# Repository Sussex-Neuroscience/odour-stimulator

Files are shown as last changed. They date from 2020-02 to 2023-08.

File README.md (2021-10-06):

# Odour stimulator - A fast, time precise open source system to deliver odours. 

## This open source stimulator is based on previous work by a different group. Their work is published  [here](https://www.pnas.org/content/111/47/16925), [here](https://www.sciencedirect.com/science/article/pii/S2589004218300646) and [here](<https://academic.oup.com/chemse/article/42/2/141/2709444>)

The image below is taken from https://academic.oup.com/chemse/article/42/2/141/2709444
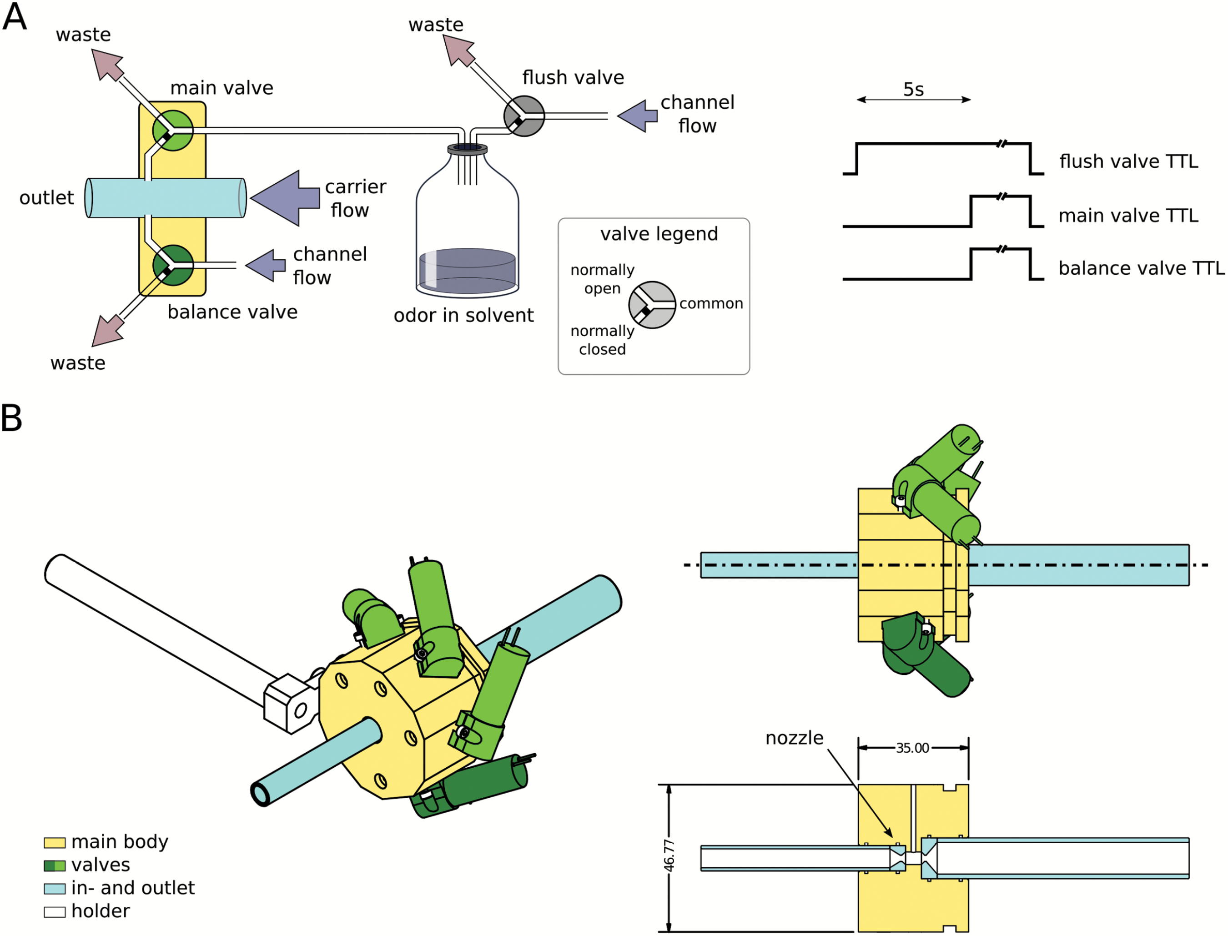
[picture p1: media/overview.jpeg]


--- 
## Some information about this project:

- developed as part of the work of the [Nowotny lab](https://www.sussex.ac.uk/research/centres/sussex-neuroscience/phd/4yearphd/supervisors/circuits-projects/thomas-nowotny-project) and it is being setup initially for experiments with flies. 
- The reason we are publicly documenting things is that since the original papers describing the stimulator came out, some enabling technology has become widely available, which makes setting this up simpler and less expensive. This write up is our attempt to document this.
- Some documentation of the orignal stimulator is already publicly available on [github already](https://github.com/grg2rsr/OlfactoryStimulator), unfortunately some of the schematics are only in PDF format (which prevents fast conversion to PCBs) and some of the CAD files are in a proprietary format, that officially can only be read with "Autodesk Inventor". Luckily there is a [plugin for FreeCad](https://github.com/jmplonka/InventorLoader/) that allows the conversion to a more open format.  This derivative will share orignal files that can be modified using open source sofware.

---

### main differences from the original papers:

- Since it would be quite expensive to reproduce the PEEK machined part they describe on the paper, we bought polypropylene filament and we printing the part. There are a couple of differences in between the two processes, and the derivatitve designs we made are optimised for printing. 
  
- Several online resources show tips and guides on how to print with this material:
 - https://www.lpfrg.com/guides/3d-printing-polypropylene/
 - https://all3dp.com/2/3d-printing-polypropylene-how-to-3d-print-with-pp/
 - https://www.simplify3d.com/support/materials-guide/polypropylene/
 - https://www.youtube.com/watch?v=yRw2mC_6A00 

- The electronics in this project but emphasis on using a microncontroller for timing control and connectivity with other devices. More specifically we are using an ESP32 and micropython to integrate the system with other devices/computers.

### repository structure:

#### repository link: https://github.com/Sussex-Neuroscience/odour-stimulator

#### tags: 
hardware,behaviour,electrophysiology,drosophila

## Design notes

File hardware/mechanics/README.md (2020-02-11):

# mechanical parts (tube fixtures, air stream nozzles, etc)

---
#### the folder [from_raiser_et_al](/from_raiser_et_al) contains the files from the github repo of the mentioned paper. They are proprietary files that can only be read with "Autodesk inventor". 

#### The content of the folder are as follows:

|File Name| Description|
|---|---|
|Assembly1.iam|Autodesk Inventor assembly that includes the spatial configuration of all the .ipt files|
|body.ipt|Main body file|
|holder.ipt|Holder for the main body|
|nozzle_big.ipt|Big nozzle placed in the main body|
|nozzle_small.ipt|Small nozzle placed in the main body|
|rod.ipt|Generic mounting rod, connects to the holder|
|table1.xls|Table summarizing the performance of the stimulator|
|tube.ipt|Glass tube, used in the Assembly1.iam for graphical purposes|
|tube_lont.ipt|Glass tube, used in the Assembly1.iam for graphical purposes|
|valve.ipt|The valve, redrawn for graphical purposes in the Assembly1.iam|

---
#### the folder [freeCad_conversion](/from_raiser_et_al/freeCad_conversion) contains the translation of those files, so that they can be opened with FreeCad. 

- this conversion is done using the following library: <https://github.com/jmplonka/InventorLoader/>

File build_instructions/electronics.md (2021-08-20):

[M4x10 screws]:parts.yaml#M4x10PanSteel
[3D printer]:parts.yaml#3DPrinter
[printed block]:parts.yaml#PrintedBlock

# Electronics

## electronic boards 

This system relies on the [BeeHive project]() for its electronic components. 

For this stimulator we are using mainly two different electronic circuits, one central hub, and some "Spike and hold" solenoid controllers.

- The central hub is responsible for receiving power, command controls from a PC and sending appropriate timing signals to the "Spike and hold" solenoid controllers.  

- The Spike and hold solenoid controllers are receiving 3.3V (or 5V) pulses that turn on the solenoid valves. The circuitry is based on a design by the solenoid manufacturer, which can be found [here](https://www.theleeco.com/engineering/electrical-engineering/lee-solenoid-valve-drive-circuit-schematics/).  
    - Briefly, the circuit generates a short fast voltage signal (spike phase) that is higher than the rating of the solenoid valve (in this case 24V), this allows for better repeatability in opening times of the solenoid as well as faster opening. When the spike phase is over, the voltage signal going to the solenoid drops down to the nominal rate of the valves (in this case 12V), which is enough to keep the valves open and avoid overheat. Once the signal to keep the valve open is done, the circuit generates a negative voltage signal that also closes the solenoid faster and more reliably.
    - An schematic fo the signal going to the solenoids can be found below (taken from the LEE company website):
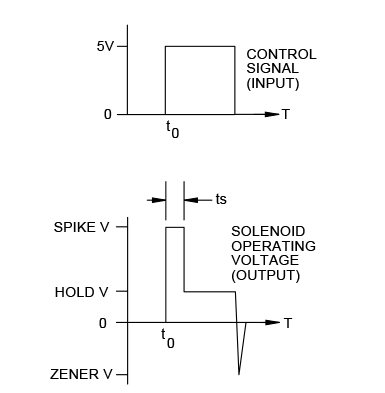
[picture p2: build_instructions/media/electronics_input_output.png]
      

{{BOM}}

## Method
This page should have some instructions for things in your project instead it just has a link for three [M4x10 screws]{Qty: 3} and another link to use [two more][M4x10 screws]{Qty: 2}.

[one block][printed block]{Qty: 1}

[3D printer][3D printer]{Qty: 1, Cat: tool}

[two more][M4x10 screws]{Qty: 2}

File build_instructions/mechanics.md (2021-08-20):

[M4x10 screws]:parts.yaml#M4x10PanSteel
[rotameterS]:parts.yaml#RotameterS
[rotameterM]:parts.yaml#RotameterM

# Mechanics

For the mechanical part of the project we are using mainly:  

- Rotameters     
- PFTE Tubing   
- Y or T connectors for the PFTE tubing     
- 3D Printed block  
- Glass tube    
- Metal plate to secure rotameters  
- holder for the printed block  

## Method
This page should have some instructions for things in your project instead it just has a link for three [M4x10 screws]{Qty: 3} and another link to use [two more][M4x10 screws]{Qty: 2}.

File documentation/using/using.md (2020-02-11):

#### use this document to guide people on using this device.

Some guidelines on what to put in this document:

1. Getting started

 - what the device should look like, things to prepare and watch out for before turning it on.

2. Turning everything on, making sure it is functioning as it should.

3. calibration steps

4. maintenance/storage information.

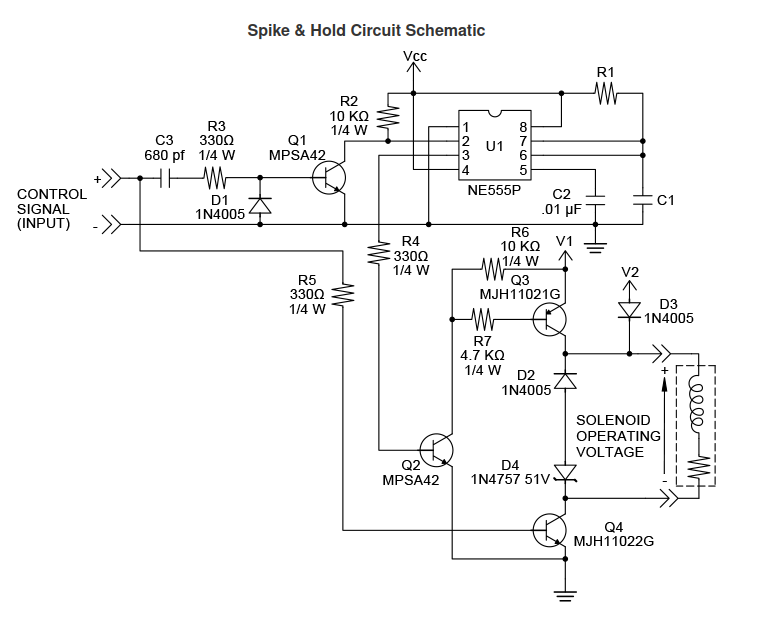
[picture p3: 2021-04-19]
media/schematics_overview.png

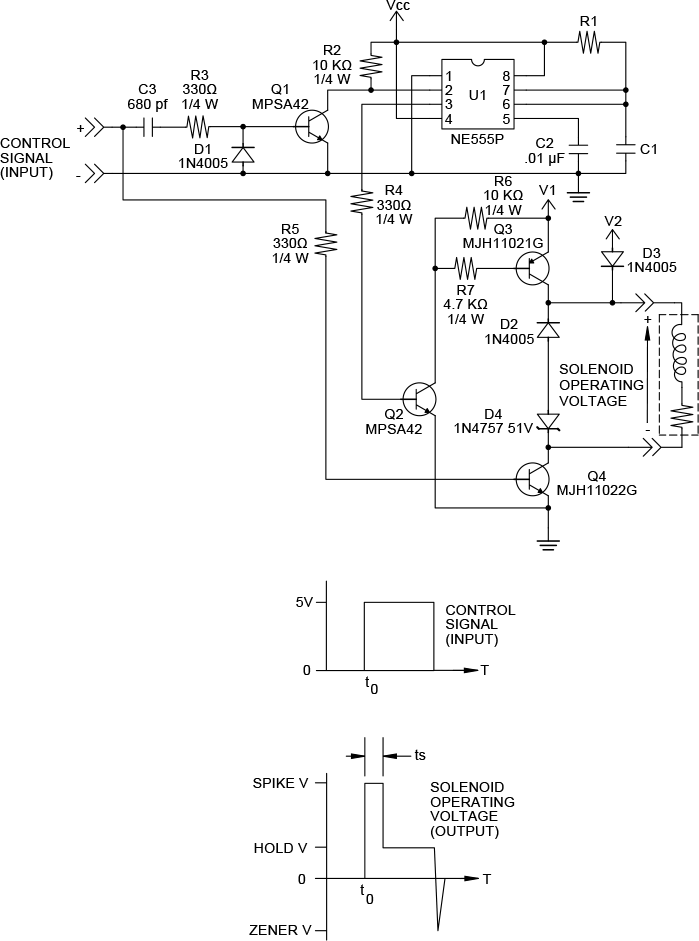
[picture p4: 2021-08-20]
media/engineering_spike-hold-circuit-schematic.png

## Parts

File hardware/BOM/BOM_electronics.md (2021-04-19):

#

| Reference | Qty  | Description | manufacturer  |MPN|Link|
|---|---|---|---|---|---|
|Solenoid valves | 5  | fast actuation 3 way solenoid valve |    [Lee](https://www.theleeco.com/)   |LHDA1221411H |<https://www.theleeco.com/products/electro-fluidic-systems/solenoid-valves/control-valves/lhd-series/3-port/face-mount/>|
|Ribbon cable| 5 metres| 10 lines ribbon cable (better if coloured) |RS components|214-0661 |<https://uk.rs-online.com/web/p/flat-ribbon-cable/2140661/>|
|electronic pressure control| 1 | ~0-3 bar, capacity > 10 L/min (the more the better, can be used for several setups)|Analyt-mtc|35898|<https://analyt-mtc.de/en/>|
|Rotameter| 1 | 0-5000ml/min|Analyt-mtc|102-05-N saphir|<https://analyt-mtc.de/en/>|
|Rotameter| 7 (at least) | 0-350ml/min|Analyt-mtc|112-02 glas|<https://analyt-mtc.de/en/>|

<br>

---
### PCB

|References              |Qty|Description                                                                        |Manufacturer     |MPN              |Manufacturer    |MPN     |Manufacturer|MPN|Manufacturer|MPN|Digikey           |Mouser|RS |Newark|Farnell|
|------------------------|---|-----------------------------------------------------------------------------------|-----------------|-----------------|----------------|--------|------------|---|------------|---|------------------|------|---|------|-------|
|C1, C2                  |2  |C Small 680pF Unpolarized capacitor, small symbol Disc D5.1mm W3.2mm P5.00mm       |Vishay           |K681K10X7RF5UH5  |                |        |            |   |            |   |BC2690CT-ND       |      |   |      |       |
|C3, C4                  |2  |C Small 10nF Unpolarized capacitor, small symbol Disc D5.1mm W3.2mm P5.00mm        |TDK corporation  |FA18C0G2A103JRU06|                |        |            |   |            |   |445-175393-1-ND   |      |   |      |       |
|C5, C6                  |2  |C Small 10µF Unpolarized capacitor, small symbol Disc D5.1mm W3.2mm P5.00mm        |AVX              |TAP106M035SCS    |                |        |            |   |            |   |478-6062-ND       |      |   |      |       |
|C11                     |1  |CP Small 680µF Polarized capacitor, small symbol Radial D10.0mm P5.00mm            |Rubycon          |35PX680MEFC10X16 |                |        |            |   |            |   |1189-1282-ND      |      |   |      |       |
|C15                     |1  |CP Small 220µF Polarized capacitor, small symbol Radial D10.0mm P5.00mm            |Panasonic        |EEU-FM1V221      |                |        |            |   |            |   |P12411-ND         |      |   |      |       |
|D1, D5, D3, D2, D6, D4  |6  |1N4005 50V 1A General Purpose Rectifier Diode, DO-41 D SOD81 P10.16mm Horizontal   |micro commercial |1N4005-TP        |                |        |            |   |            |   |1N4005-TPMSCT-ND  |      |   |      |       |
|D7, D8                  |2  |1N47xxA 1300mW Zener Diode, DO-41 D SOD81 P10.16mm Horizontal                      |Vishay           |1N4757A-TR       |                |        |            |   |            |   |1N4757AVSCT-ND    |      |   |      |       |
|D17                     |1  |1N5820 20V 3A Schottky Barrier Rectifier Diode, DO-201AD D P15.24mm Horizontal     |SMC              |SB5100TA         |                |        |            |   |            |   |1655-1524-1-ND    |      |   |      |       |
|H4, H3, H1, H2          |4  |MountingHole Mounting Hole without connection 3.2mm M3                             |                 |                 |                |        |            |   |            |   |                  |      |   |      |       |
|J1, J2                  |2  |Conn 01x02 Female single row, 01x02 P2.54mm Vertical                               |Sullins          |PPTC101LFBN-RC   |                |        |            |   |            |   |S7008-ND          |      |   |      |       |
|J3, J4                  |2  |Screw Terminal 01x02 P2.54mm Vertical                                              |                 |                 |                |        |            |   |            |   |                  |      |   |      |       |
|J9                      |1  |Barrel Jack MountingPin DC with a mounting pin 5.5mmODx2.1mmID PJ-202A             |CUI devices      |PJ-202AH         |                |        |            |   |            |   |CP-202AH-ND       |      |   |      |       |
|L1                      |1  |L 33µH Inductor Radial D7.5mm P3.50mm Fastron 07P                                  |Wuerth           |7447471330       |                |        |            |   |            |   |732-3415-ND       |      |   |      |       |
|Q1, Q2                  |2  |Q PNP Darlington BCE MJH11021G transistor, base/collector/emitter TO-247-3 Vertical|ON semiconductors|MJH11021G        |                |        |            |   |            |   |MJH11021GOS-ND    |      |   |      |       |
|Q5, Q6, Q3, Q4          |4  |MPSA42 TRANS NPN 300V 0.5A TO-92 TO-92L Inline Wide                                |ON semiconductors|MPSA42           |ON semiconductor|KSP42BU |            |   |            |   |KSP42BU-ND        |      |   |      |       |
|Q7, Q8                  |2  |Q NPN Darlington BCE MJH11022G transistor, base/collector/emitter TO-247-3 Vertical|ON semiconductors|MJH11022G        |                |        |            |   |            |   |MJH11022GOS-ND    |      |   |      |       |
|R1, R9, R2, R10         |4  |R Small 10k Resistor, small symbol Axial DIN0411 L9.9mm D3.6mm P12.70mm Horizontal |Stackpole        |CF14JT10K0       |                |        |            |   |            |   |CF14JT10K0CT-ND   |      |   |      |       |
|R3, R4                  |2  |R Small 4.7k Resistor, small symbol Axial DIN0411 L9.9mm D3.6mm P12.70mm Horizontal|Stackpole        |CF14JT4K70       |                |        |            |   |            |   |CF14JT4K70CT-ND   |      |   |      |       |
|R7, R11, R5, R8, R12, R6|6  |R Small 330 Resistor, small symbol Axial DIN0411 L9.9mm D3.6mm P12.70mm Horizontal |Stackpole        |CF14JT330R       |                |        |            |   |            |   |CF14JT330RCT-ND   |      |   |      |       |
|R13, R14                |2  |R Small 2k Resistor, small symbol Axial DIN0411 L9.9mm D3.6mm P12.70mm Horizontal  |Stackpole        |CF14JT2K00       |                |        |            |   |            |   |CF14JT2K00CT-ND   |      |   |      |       |
|R15                     |1  |R Small 1k Resistor, small symbol Axial DIN0411 L9.9mm D3.6mm P12.70mm Horizontal  |Stackpole        |CF14JT1K00       |                |        |            |   |            |   |CF14JT1K00CT-ND   |      |   |      |       |
|R16                     |1  |R Small 9.1k Resistor, small symbol Axial DIN0411 L9.9mm D3.6mm P12.70mm Horizontal|Stackpole        |RNMF14FAD9K10    |                |        |            |   |            |   |RNMF14FAD9K10CT-ND|      |   |      |       |
|U1, U2                  |2  |LM555xM Precision Timers, 555 compatible, SOIC-8 DIP-8 W7.62mm LongPads            |Texas instruments|NA555P           |                |        |            |   |            |   |296-21753-5-ND    |      |   |      |       |
|U5                      |1  |LM2596T-ADJ 12V 3A 150kHz Step-Down Voltage Regulator, TO-220 TO-220-5             |Texas instruments|LM2596T-ADJ/LF02 |                |        |            |   |            |   |296-49677-ND      |      |   |      |       |

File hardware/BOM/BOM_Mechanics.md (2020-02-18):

#

## Glossary

ID - Internal diametre  
OD - External diametre

| Reference | Qty  | Description | supplier  |MPN|Link|
|---|---|---|---|---|---|
|Female Luer | 14  | x10-32 UNF thread, PC - (polycarbonate?) seems to be this <https://www.fishersci.co.uk/shop/products/polycarbonate-luer-fitting-1/11746008> | novodirect   |YO-45501-60|company website leads to <https://www.fishersci.co.uk/gb/en/home.html>|
|Male Luer Adapter| 40 pieces | luer to tube adapter (~1.2mm ID or ~1/16 inch) |Cole-Parmer|15252400 |<https://www.fishersci.co.uk/shop/products/polypropylene-male-luer-adapters-4/15252400>|
|Teflon tubing|X metres|original from paper has been discontinued. 4mm ID 5mm OD is what comes closer |[VWR](<https://uk.vwr.com>)|DENE3400405|<https://uk.vwr.com/store/product/576865/tubing-ptfe>|
|Teflon tubing|10 metres|original from paper has been discontinued. 1mm ID 2mm OD is what comes closer |[VWR](<https://uk.vwr.com>)|DENE3400102|<https://uk.vwr.com/store/product/576865/tubing-ptfe>|
|Y shaped connector|20|for 4mm ID tubing|[VWR](<https://uk.vwr.com>)|229-0723|https://uk.vwr.com/store/catalog/product.jsp?catalog_number=229-0723|
|Tube clamps| 20 |stepless flow control|[VWR](<https://uk.vwr.com>) |229-0117|<https://uk.vwr.com/store/product/7652160/tubing-clamps-stop-it>|
|Glass vials | 20 |12 ml glass vials (preferentially with rubber/silicone lid) |[VWR](<https://uk.vwr.com>) | 548-0820|<https://uk.vwr.com/store/catalog/product.jsp?catalog_number=548-0820>|
|Glass vials caps| 20 |screw caps with rubber/silicone part for needle entry |[VWR](<https://uk.vwr.com>) | 548-3335|<https://uk.vwr.com/store/catalog/product.jsp?catalog_number=548-0820>|
| Needles | 100 |18G X 1 1/2 |[VWR](<https://uk.vwr.com>) |613-5396|<https://uk.vwr.com/store/product/16614798/hypodermic-needles-aganitm>|
| Needles | 20|14G 2X40mm |[VWR](<https://uk.vwr.com>) | HSWA8300013707 |<https://uk.vwr.com/store/product/7210520/hypodermic-needles-fine-ject-for-single-use>|
| O-ring | 1 | 12mm ID 15mm OD silicone  |[RS](<https://uk.rs-online.com>) | 0128849 |<https://uk.rs-online.com/web/p/seals-o-rings/0128849/>|
| O-ring | 1 | 7.5mm ID 11mm OD silicone |[RS](<https://uk.rs-online.com>) | 5279790 |<https://uk.rs-online.com/web/p/seals-o-rings/5279790/>|

glass tube 7 mm ID, 10 mm OD, 80 mm length  
glass tube 4 mm ID, 7 mm OD, 80 mm length  

#### note : The rows indicated with !! are as on the original bill of materials, but they seem to be a duplicate entry.

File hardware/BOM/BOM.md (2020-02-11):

#### Create BOM files for the equipment

e recommend creating different files:

<br>
- Electronic_BOM.csv: table containing all the integrated circuits(IC) necessary to populate the PCB (when one is present). We suggest using the format used by [kitspace.org](kitspace.org), so that people can easily order parts from different manufacturers.
<br>

<br>

- Mechanical_BOM.csv: Table containing all the mechanical parts necessary to build the equipment. Include here screws, printed parts, tubes, etc. See example below for fields

<br>

|part name| function  | quantity  |  obs.  |supplier|supplier number|link|
|---|---|---|---|---|---|---|
|M6x1 hex screws | used for holding motor in place  | 5  |  these could be substituted by flathead screws  |digikey| RPC6208-ND |<https://www.digikey.co.uk/product-detail/en/essentra-components/SHSM6L16A/RPC6208-ND/9343049> |

<br>

- Tools_BOM.csv: table containing all tools used for the build. Pliers, hammer, etc.

<br>

|part name| function  | quantity  |  obs.  |supplier|supplier number|link|
|---|---|---|---|---|---|---|
|Nose needle Pliers  | hold components while soldering  | 1  |    regular pliers would also work   |digikey|L4VN-ND  |<https://www.digikey.co.uk/product-detail/en/apex-tool-group/L4VN/L4VN-ND/8021129> |

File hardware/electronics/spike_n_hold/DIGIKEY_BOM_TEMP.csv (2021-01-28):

Reference | Value | Footprint | Datasheet | Category | DK_Datasheet_Link | DK_Detail_Page | Description | Digi-Key_PN | Family | MPN | Manufacturer | Status
Q1 | MJH11021G |  | ~
Q7 | MJH11022G |  | ~
R3 | 4.7k |  | ~
R1 | 10k |  | ~
R7 | 330 |  | ~
D1 | 1N4005 | Diode_THT:D_DO-41_SOD81_P10.16mm_Horizontal | http://www.vishay.com/docs/88503/1n4001.pdf
D5 | 1N4005 | Diode_THT:D_DO-41_SOD81_P10.16mm_Horizontal | http://www.vishay.com/docs/88503/1n4001.pdf
D7 | 1N47xxA | Diode_THT:D_DO-41_SOD81_P10.16mm_Horizontal | https://www.vishay.com/docs/85816/1n4728a.pdf
J3 | to_solenoid_2 | Connector_PinHeader_2.54mm:PinHeader_1x02_P2.54mm_Vertical | ~
R11 | 330 |  | ~
Q5 | MPSA42 | digikey-footprints:TO-92-3 | https://www.onsemi.com/pub/Collateral/MPSA42-D.PDF | Discrete Semiconductor Products | https://www.onsemi.com/pub/Collateral/MPSA42-D.PDF | /product-detail/en/on-semiconductor/MPSA42/MPSA42FS-ND/32397 | TRANS NPN 300V 0.5A TO-92 | MPSA42FS-ND | Transistors - Bipolar (BJT) - Single | MPSA42 | ON Semiconductor | Active
Q3 | MPSA42 | Package_TO_SOT_THT:TO-92_Inline | http://www.onsemi.com/pub_link/Collateral/MPSA42-D.PDF
D3 | 1N4005 | Diode_THT:D_DO-41_SOD81_P10.16mm_Horizontal | http://www.vishay.com/docs/88503/1n4001.pdf
R5 | 330 |  | ~
J1 | input_trigger_2 | Connector_PinHeader_2.54mm:PinHeader_1x02_P2.54mm_Vertical | ~
C1 | 680pF | Capacitor_THT:C_Disc_D5.1mm_W3.2mm_P5.00mm | ~
C5 | 10µF |  | ~
C3 | 10nF |  | ~
U1 | LM555xM | Package_DIP:DIP-8_W7.62mm_LongPads | http://www.ti.com/lit/ds/symlink/lm555.pdf
R9 | 10k |  | ~
R13 | 2k |  | ~
Q9 | MJH11021G |  | ~
Q15 | MJH11022G |  | ~
R16 | 4.7k |  | ~
R15 | 10k |  | ~
R21 | 330 |  | ~
D9 | 1N4005 | Diode_THT:D_DO-41_SOD81_P10.16mm_Horizontal | http://www.vishay.com/docs/88503/1n4001.pdf
D12 | 1N4005 | Diode_THT:D_DO-41_SOD81_P10.16mm_Horizontal | http://www.vishay.com/docs/88503/1n4001.pdf
D15 | 1N47xxA | Diode_THT:D_DO-41_SOD81_P10.16mm_Horizontal | https://www.vishay.com/docs/85816/1n4728a.pdf
J7 | to_solenoid_4 | Connector_PinHeader_2.54mm:PinHeader_1x02_P2.54mm_Vertical | ~
R25 | 330 |  | ~
Q13 | MPSA42 | digikey-footprints:TO-92-3 | https://www.onsemi.com/pub/Collateral/MPSA42-D.PDF | Discrete Semiconductor Products | https://www.onsemi.com/pub/Collateral/MPSA42-D.PDF | /product-detail/en/on-semiconductor/MPSA42/MPSA42FS-ND/32397 | TRANS NPN 300V 0.5A TO-92 | MPSA42FS-ND | Transistors - Bipolar (BJT) - Single | MPSA42 | ON Semiconductor | Active
Q11 | MPSA42 | Package_TO_SOT_THT:TO-92_Inline | http://www.onsemi.com/pub_link/Collateral/MPSA42-D.PDF
D10 | 1N4005 | Diode_THT:D_DO-41_SOD81_P10.16mm_Horizontal | http://www.vishay.com/docs/88503/1n4001.pdf
R19 | 330 |  | ~
J5 | input_trigger_4 | Connector_PinHeader_2.54mm:PinHeader_1x02_P2.54mm_Vertical | ~
C7 | 680pF | Capacitor_THT:C_Disc_D5.1mm_W3.2mm_P5.00mm | ~
C12 | 10µF |  | ~
C9 | 10nF |  | ~
U3 | LM555xM | Package_DIP:DIP-8_W7.62mm_LongPads | http://www.ti.com/lit/ds/symlink/lm555.pdf
R22 | 10k |  | ~
R27 | 2k |  | ~
Q17 | MJH11021G |  | ~
Q23 | MJH11022G |  | ~
R31 | 4.7k |  | ~
R29 | 10k |  | ~
R35 | 330 |  | ~
D18 | 1N4005 | Diode_THT:D_DO-41_SOD81_P10.16mm_Horizontal | http://www.vishay.com/docs/88503/1n4001.pdf
D22 | 1N4005 | Diode_THT:D_DO-41_SOD81_P10.16mm_Horizontal | http://www.vishay.com/docs/88503/1n4001.pdf
D24 | 1N47xxA | Diode_THT:D_DO-41_SOD81_P10.16mm_Horizontal | https://www.vishay.com/docs/85816/1n4728a.pdf
J12 | to_solenoid_6 | Connector_PinHeader_2.54mm:PinHeader_1x02_P2.54mm_Vertical | ~
R39 | 330 |  | ~
Q21 | MPSA42 | digikey-footprints:TO-92-3 | https://www.onsemi.com/pub/Collateral/MPSA42-D.PDF | Discrete Semiconductor Products | https://www.onsemi.com/pub/Collateral/MPSA42-D.PDF | /product-detail/en/on-semiconductor/MPSA42/MPSA42FS-ND/32397 | TRANS NPN 300V 0.5A TO-92 | MPSA42FS-ND | Transistors - Bipolar (BJT) - Single | MPSA42 | ON Semiconductor | Active
Q19 | MPSA42 | Package_TO_SOT_THT:TO-92_Inline | http://www.onsemi.com/pub_link/Collateral/MPSA42-D.PDF
D19 | 1N4005 | Diode_THT:D_DO-41_SOD81_P10.16mm_Horizontal | http://www.vishay.com/docs/88503/1n4001.pdf
R33 | 330 |  | ~
J10 | input_trigger_6 | Connector_PinHeader_2.54mm:PinHeader_1x02_P2.54mm_Vertical | ~
C14 | 680pF | Capacitor_THT:C_Disc_D5.1mm_W3.2mm_P5.00mm | ~
C19 | 10µF |  | ~
C17 | 10nF |  | ~
U6 | LM555xM | Package_DIP:DIP-8_W7.62mm_LongPads | http://www.ti.com/lit/ds/symlink/lm555.pdf
R37 | 10k |  | ~
R41 | 2k |  | ~
Q2 | MJH11021G |  | ~
Q8 | MJH11022G |  | ~
R4 | 4.7k |  | ~
R2 | 10k |  | ~
R8 | 330 |  | ~
D2 | 1N4005 | Diode_THT:D_DO-41_SOD81_P10.16mm_Horizontal | http://www.vishay.com/docs/88503/1n4001.pdf
D6 | 1N4005 | Diode_THT:D_DO-41_SOD81_P10.16mm_Horizontal | http://www.vishay.com/docs/88503/1n4001.pdf
D8 | 1N47xxA | Diode_THT:D_DO-41_SOD81_P10.16mm_Horizontal | https://www.vishay.com/docs/85816/1n4728a.pdf
J4 | to_solenoid_1 | Connector_PinHeader_2.54mm:PinHeader_1x02_P2.54mm_Vertical | ~
R12 | 330 |  | ~
Q6 | MPSA42 | digikey-footprints:TO-92-3 | https://www.onsemi.com/pub/Collateral/MPSA42-D.PDF | Discrete Semiconductor Products | https://www.onsemi.com/pub/Collateral/MPSA42-D.PDF | /product-detail/en/on-semiconductor/MPSA42/MPSA42FS-ND/32397 | TRANS NPN 300V 0.5A TO-92 | MPSA42FS-ND | Transistors - Bipolar (BJT) - Single | MPSA42 | ON Semiconductor | Active
Q4 | MPSA42 | Package_TO_SOT_THT:TO-92_Inline | http://www.onsemi.com/pub_link/Collateral/MPSA42-D.PDF
D4 | 1N4005 | Diode_THT:D_DO-41_SOD81_P10.16mm_Horizontal | http://www.vishay.com/docs/88503/1n4001.pdf
R6 | 330 |  | ~
J2 | input_trigger_1 | Connector_PinHeader_2.54mm:PinHeader_1x02_P2.54mm_Vertical | ~
C2 | 680pF | Capacitor_THT:C_Disc_D5.1mm_W3.2mm_P5.00mm | ~
C6 | 10µF |  | ~
C4 | 10nF |  | ~
U2 | LM555xM | Package_DIP:DIP-8_W7.62mm_LongPads | http://www.ti.com/lit/ds/symlink/lm555.pdf
R10 | 10k |  | ~
R14 | 2k |  | ~
Q18 | MJH11021G |  | ~
Q24 | MJH11022G |  | ~
R32 | 4.7k |  | ~
R30 | 10k |  | ~
R36 | 330 |  | ~
D20 | 1N4005 | Diode_THT:D_DO-41_SOD81_P10.16mm_Horizontal | http://www.vishay.com/docs/88503/1n4001.pdf
D23 | 1N4005 | Diode_THT:D_DO-41_SOD81_P10.16mm_Horizontal | http://www.vishay.com/docs/88503/1n4001.pdf
D25 | 1N47xxA | Diode_THT:D_DO-41_SOD81_P10.16mm_Horizontal | https://www.vishay.com/docs/85816/1n4728a.pdf
J13 | to_solenoid_5 | Connector_PinHeader_2.54mm:PinHeader_1x02_P2.54mm_Vertical | ~
R40 | 330 |  | ~
Q22 | MPSA42 | digikey-footprints:TO-92-3 | https://www.onsemi.com/pub/Collateral/MPSA42-D.PDF | Discrete Semiconductor Products | https://www.onsemi.com/pub/Collateral/MPSA42-D.PDF | /product-detail/en/on-semiconductor/MPSA42/MPSA42FS-ND/32397 | TRANS NPN 300V 0.5A TO-92 | MPSA42FS-ND | Transistors - Bipolar (BJT) - Single | MPSA42 | ON Semiconductor | Active
Q20 | MPSA42 | Package_TO_SOT_THT:TO-92_Inline | http://www.onsemi.com/pub_link/Collateral/MPSA42-D.PDF
D21 | 1N4005 | Diode_THT:D_DO-41_SOD81_P10.16mm_Horizontal | http://www.vishay.com/docs/88503/1n4001.pdf
R34 | 330 |  | ~
J11 | input_trigger_5 | Connector_PinHeader_2.54mm:PinHeader_1x02_P2.54mm_Vertical | ~
C16 | 680pF | Capacitor_THT:C_Disc_D5.1mm_W3.2mm_P5.00mm | ~
C20 | 10µF |  | ~
C18 | 10nF |  | ~
U7 | LM555xM | Package_DIP:DIP-8_W7.62mm_LongPads | http://www.ti.com/lit/ds/symlink/lm555.pdf
R38 | 10k |  | ~
R42 | 2k |  | ~
Q10 | MJH11021G |  | ~
Q16 | MJH11022G |  | ~
R18 | 4.7k |  | ~
R17 | 10k |  | ~
R23 | 330 |  | ~
D11 | 1N4005 | Diode_THT:D_DO-41_SOD81_P10.16mm_Horizontal | http://www.vishay.com/docs/88503/1n4001.pdf
D14 | 1N4005 | Diode_THT:D_DO-41_SOD81_P10.16mm_Horizontal | http://www.vishay.com/docs/88503/1n4001.pdf
D16 | 1N47xxA | Diode_THT:D_DO-41_SOD81_P10.16mm_Horizontal | https://www.vishay.com/docs/85816/1n4728a.pdf
J8 | to_solenoid_3 | Connector_PinHeader_2.54mm:PinHeader_1x02_P2.54mm_Vertical | ~
R26 | 330 |  | ~
Q14 | MPSA42 | digikey-footprints:TO-92-3 | https://www.onsemi.com/pub/Collateral/MPSA42-D.PDF | Discrete Semiconductor Products | https://www.onsemi.com/pub/Collateral/MPSA42-D.PDF | /product-detail/en/on-semiconductor/MPSA42/MPSA42FS-ND/32397 | TRANS NPN 300V 0.5A TO-92 | MPSA42FS-ND | Transistors - Bipolar (BJT) - Single | MPSA42 | ON Semiconductor | Active
Q12 | MPSA42 | Package_TO_SOT_THT:TO-92_Inline | http://www.onsemi.com/pub_link/Collateral/MPSA42-D.PDF
D13 | 1N4005 | Diode_THT:D_DO-41_SOD81_P10.16mm_Horizontal | http://www.vishay.com/docs/88503/1n4001.pdf
R20 | 330 |  | ~
J6 | input_trigger_3 | Connector_PinHeader_2.54mm:PinHeader_1x02_P2.54mm_Vertical | ~
C8 | 680pF | Capacitor_THT:C_Disc_D5.1mm_W3.2mm_P5.00mm | ~
C13 | 10µF |  | ~
C10 | 10nF |  | ~
U4 | LM555xM | Package_DIP:DIP-8_W7.62mm_LongPads | http://www.ti.com/lit/ds/symlink/lm555.pdf
R24 | 10k |  | ~
R28 | 2k |  | ~
U5 | LM2596T-12 | Package_TO_SOT_THT:TO-220-5_P3.4x3.7mm_StaggerOdd_Lead3.8mm_Vertical | http://www.ti.com/lit/ds/symlink/lm2596.pdf
D17 | 1N5820 | Diode_THT:D_DO-201AD_P15.24mm_Horizontal | http://www.vishay.com/docs/88526/1n5820.pdf
L1 | 33µH | Inductor_THT:L_Radial_D7.5mm_P3.50mm_Fastron_07P | ~
C11 | 680µF |  | ~
C15 | 220µF |  | ~
J9 | Barrel_Jack_MountingPin | digikey:Barrel_Jack_5.5mmODx2.1mmID_PJ-202A | ~

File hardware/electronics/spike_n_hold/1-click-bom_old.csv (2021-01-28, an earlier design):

References | Qty | Description
C1, C7, C14, C2, C16, C8 | 6 | C Small 680pF Unpolarized capacitor, small symbol Disc D5.1mm W3.2mm P5.00mm | https://www.digikey.co.uk/product-detail/en/vishay-beyschlag-draloric-bc-components/K681K10X7RF5UH5/BC2690CT-ND/2356904
C3, C9, C17, C4, C18, C10 | 6 | C Small 10nF Unpolarized capacitor, small symbol | https://www.digikey.co.uk/product-detail/en/vishay-beyschlag-draloric-bc-components/K103K10X7RF5UH5/BC2662CT-ND/2356876
C5, C12, C19, C6, C20, C13 | 6 | C Small 10µF Unpolarized capacitor, small symbol
C11 | 1 | CP Small 680µF Polarized capacitor, small symbol
C15 | 1 | CP Small 220µF Polarized capacitor, small symbol
D1, D5, D3, D9, D12, D10, D18, D22, D19, D2, D6, D4, D20, D23, D21, D11, D14, D13 | 18 | 1N4005 50V 1A General Purpose Rectifier Diode, DO-41 D SOD81 P10.16mm Horizontal
D7, D15, D24, D8, D25, D16 | 6 | 1N47xxA 1300mW Zener Diode, DO-41 D SOD81 P10.16mm Horizontal
D17 | 1 | 1N5820 20V 3A Schottky Barrier Rectifier Diode, DO-201AD D P15.24mm Horizontal
J1 | 1 | Conn 01x02 Female input trigger 2 Generic connector, single row, 01x02, script generated (kicad-library-utils/schlib/autogen/connector/) PinHeader 1x02 P2.54mm Vertical
J2 | 1 | Conn 01x02 Female input trigger 1 Generic connector, single row, 01x02, script generated (kicad-library-utils/schlib/autogen/connector/) PinHeader 1x02 P2.54mm Vertical
J3 | 1 | Screw Terminal 01x02 to solenoid 2 Generic screw terminal, single row, 01x02, script generated (kicad-library-utils/schlib/autogen/connector/) PinHeader 1x02 P2.54mm Vertical
J4 | 1 | Screw Terminal 01x02 to solenoid 1 Generic screw terminal, single row, 01x02, script generated (kicad-library-utils/schlib/autogen/connector/) PinHeader 1x02 P2.54mm Vertical
J5 | 1 | Conn 01x02 Female input trigger 4 Generic connector, single row, 01x02, script generated (kicad-library-utils/schlib/autogen/connector/) PinHeader 1x02 P2.54mm Vertical
J6 | 1 | Conn 01x02 Female input trigger 3 Generic connector, single row, 01x02, script generated (kicad-library-utils/schlib/autogen/connector/) PinHeader 1x02 P2.54mm Vertical
J7 | 1 | Screw Terminal 01x02 to solenoid 4 Generic screw terminal, single row, 01x02, script generated (kicad-library-utils/schlib/autogen/connector/) PinHeader 1x02 P2.54mm Vertical
J8 | 1 | Screw Terminal 01x02 to solenoid 3 Generic screw terminal, single row, 01x02, script generated (kicad-library-utils/schlib/autogen/connector/) PinHeader 1x02 P2.54mm Vertical
J9 | 1 | Barrel Jack MountingPin DC with a mounting pin 5.5mmODx2.1mmID PJ-202A
J10 | 1 | Conn 01x02 Female input trigger 6 Generic connector, single row, 01x02, script generated (kicad-library-utils/schlib/autogen/connector/) PinHeader 1x02 P2.54mm Vertical
J11 | 1 | Conn 01x02 Female input trigger 5 Generic connector, single row, 01x02, script generated (kicad-library-utils/schlib/autogen/connector/) PinHeader 1x02 P2.54mm Vertical
J12 | 1 | Screw Terminal 01x02 to solenoid 6 Generic screw terminal, single row, 01x02, script generated (kicad-library-utils/schlib/autogen/connector/) PinHeader 1x02 P2.54mm Vertical
J13 | 1 | Screw Terminal 01x02 to solenoid 5 Generic screw terminal, single row, 01x02, script generated (kicad-library-utils/schlib/autogen/connector/) PinHeader 1x02 P2.54mm Vertical
L1 | 1 | L 33µH Inductor Radial D7.5mm P3.50mm Fastron 07P
Q1, Q9, Q17, Q2, Q18, Q10 | 6 | Q PNP Darlington BCE MJH11021G transistor, base/collector/emitter | https://www.digikey.co.uk/products/en?keywords=MJH11021G
Q3, Q11, Q19, Q4, Q20, Q12 | 6 | MPSA42 0.5A Ic, 300V Vce, NPN High Voltage Transistor, TO-92 Inline
Q5, Q13, Q21, Q6, Q22, Q14 | 6 | MPSA42 TRANS NPN 300V 0.5A TO-92 TO-92-3
Q7, Q15, Q23, Q8, Q24, Q16 | 6 | Q NPN Darlington BCE MJH11022G transistor, base/collector/emitter | https://www.digikey.co.uk/products/en?keywords=MJH11022G
R1, R9, R15, R22, R29, R37, R2, R10, R30, R38, R17, R24 | 12 | R Small 10k Resistor, small symbol
R3, R16, R31, R4, R32, R18 | 6 | R Small 4.7k Resistor, small symbol
R7, R11, R5, R21, R25, R19, R35, R39, R33, R8, R12, R6, R36, R40, R34, R23, R26, R20 | 18 | R Small 330 Resistor, small symbol
R13, R27, R41, R14, R42, R28 | 6 | R Small 2k Resistor, small symbol
U1, U3, U6, U2, U7, U4 | 6 | LM555xM Precision Timers, 555 compatible, SOIC-8 DIP-8 W7.62mm LongPads
U5 | 1 | LM2596T-12 12V 3A 150kHz Step-Down Voltage Regulator, TO-220 TO-220-5 P3.4x3.7mm StaggerOdd Lead3.8mm Vertical

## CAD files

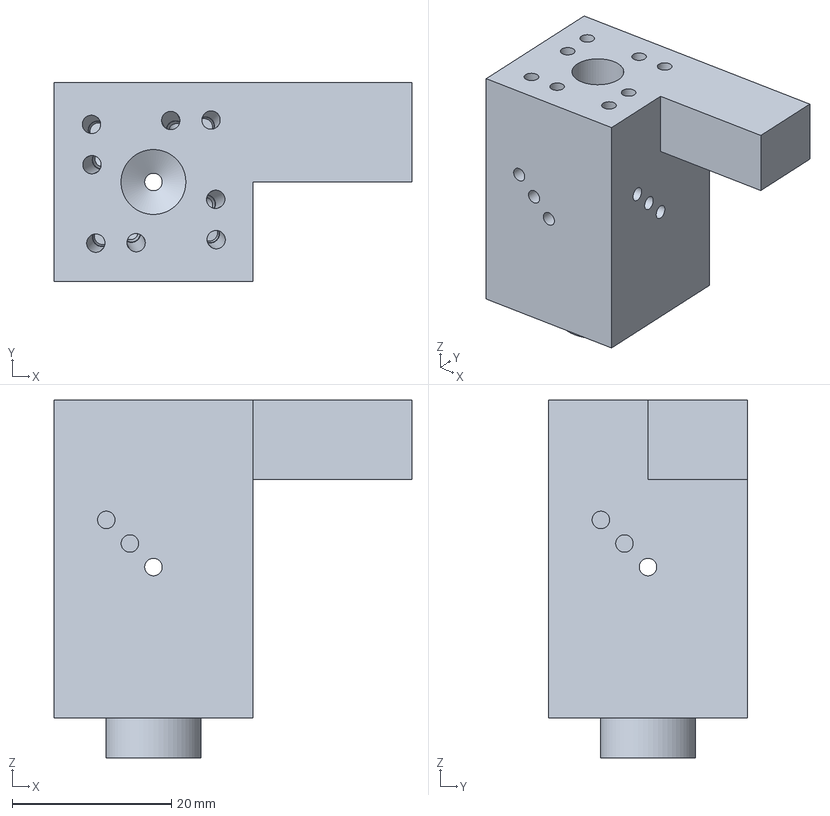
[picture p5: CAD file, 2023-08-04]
hardware/mechanics/new_system/stls/main_body.3mf
45.0 x 25.0 x 45.0 mm

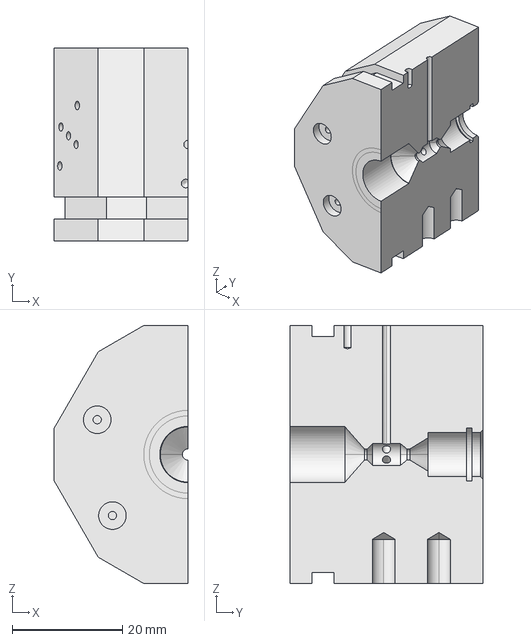
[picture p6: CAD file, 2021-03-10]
hardware/mechanics/new_system/v0.1/main_halved_for_measurements.FCStd
24.3 x 35.0 x 46.8 mm

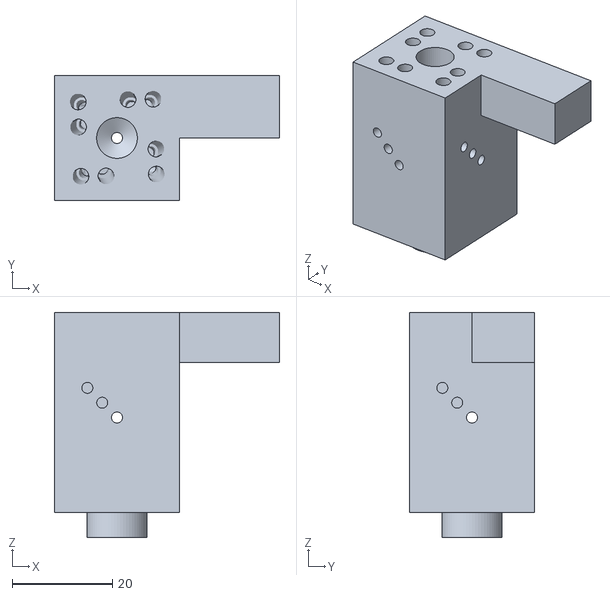
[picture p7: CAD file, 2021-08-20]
hardware/mechanics/new_system/stls/main_body_w_holder.stl
45.0 x 25.0 x 45.0

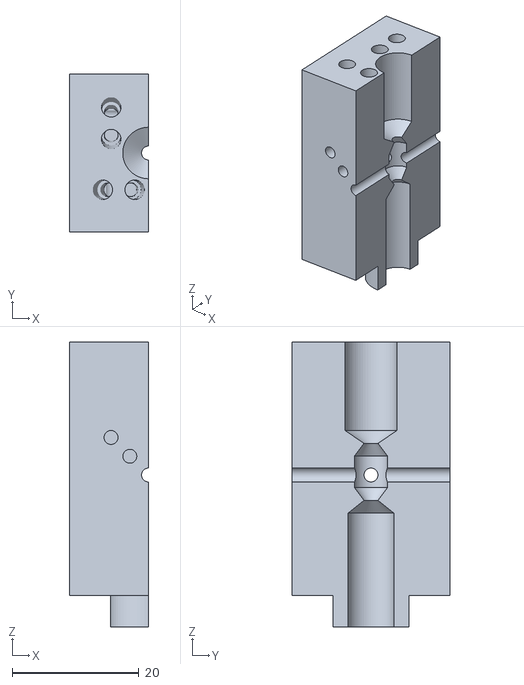
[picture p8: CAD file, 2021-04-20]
hardware/mechanics/new_system/stls/main_body_half.stl
12.5 x 25.0 x 45.0

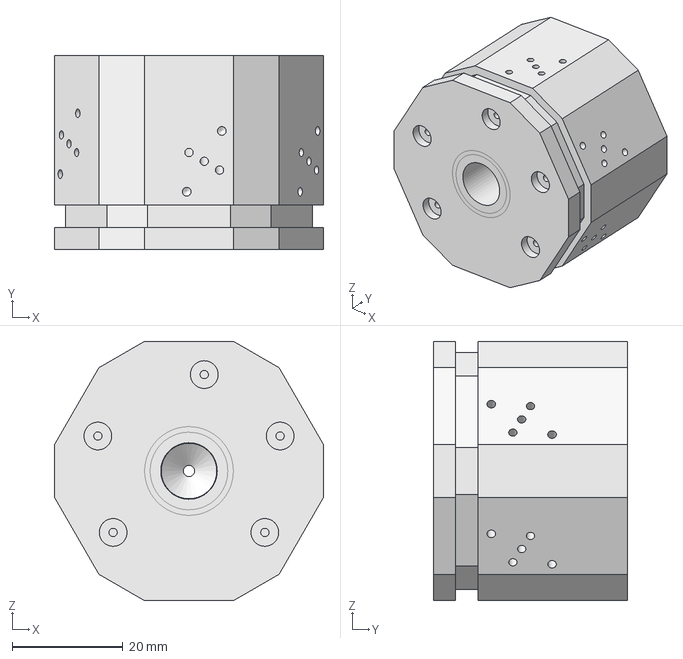
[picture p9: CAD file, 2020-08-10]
hardware/mechanics/new_system/v0.1/main.FCStd
48.5 x 35.0 x 46.8 mm

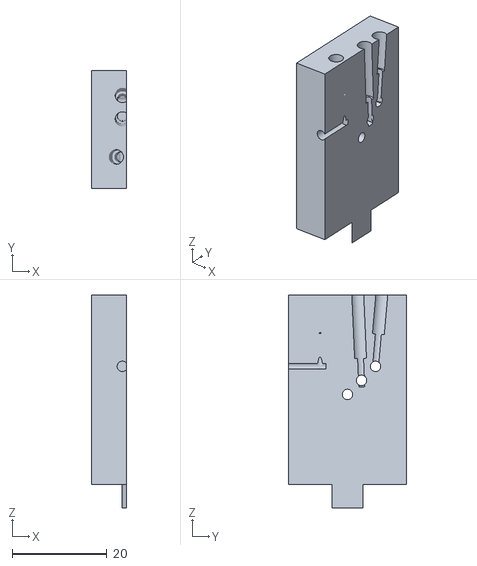
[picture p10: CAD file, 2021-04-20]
hardware/mechanics/new_system/stls/main_body_cutout1.stl
7.50 x 25.0 x 45.0

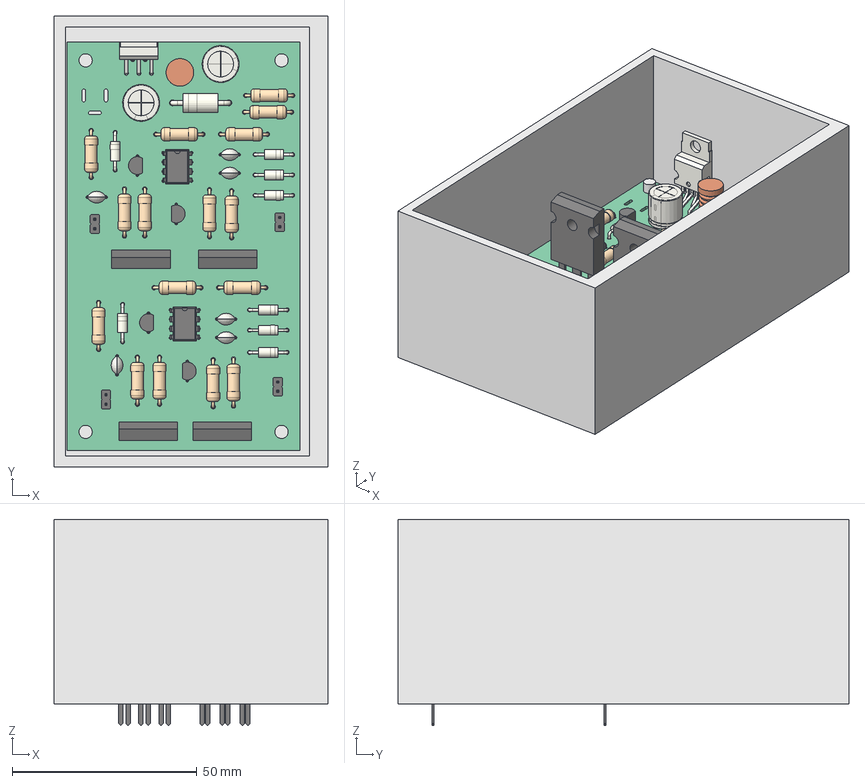
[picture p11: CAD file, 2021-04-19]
hardware/mechanics/electronics_box.FCStd
74.0 x 122.0 x 55.8 mm
Pcb_ab1c
D4_D_DO-41_SOD81_P10.16mm_Horizontal_60125312
C1_C_Disc_D51mm_W32mm_P500mm_60124F99
C2_C_Disc_D51mm_W32mm_P500mm_60129F43
C3_C_Disc_D51mm_W32mm_P500mm_60124FC3
C4_C_Disc_D51mm_W32mm_P500mm_60124FD8
C5_C_Disc_D51mm_W32mm_P500mm_60124FED
C6_C_Disc_D51mm_W32mm_P500mm_60125002
C11_CP_Radial_D100mm_P500mm_60125122
C15_CP_Radial_D100mm_P500mm_6012522D
D1_D_DO-41_SOD81_P10.16mm_Horizontal_601252B5
D2_D_DO-41_SOD81_P10.16mm_Horizontal_601252D4
D3_D_DO-41_SOD81_P10.16mm_Horizontal_601252F3
D5_D_DO-41_SOD81_P10.16mm_Horizontal_60125331
D6_D_DO-41_SOD81_P10.16mm_Horizontal_60125350
D7_D_DO-41_SOD81_P10.16mm_Horizontal_6012536F
D8_D_DO-41_SOD81_P10.16mm_Horizontal_6012538E
D17_D_DO-201AD_P15.24mm_Horizontal_601254A5
J1_PinHeader_1x02_P254mm_Vertical_601255B3
J2_PinHeader_1x02_P254mm_Vertical_601255C9
J3_PinHeader_1x02_P254mm_Vertical_601255DF
J4_PinHeader_1x02_P254mm_Vertical_601255F5
L1_L_Radial_D7.5mm_P3.50mm_Fastron_07P_601256C9
Q1_TO-247-3_Vertical_601256E1
Q2_TO-247-3_Vertical_601256F9
Q7_TO-247-3_Vertical_60125711
Q8_TO-247-3_Vertical_60125729
R1_R_Axial_DIN0411_L99mm_D36mm_P1270mm_Horizontal_60125800
R2_R_Axial_DIN0411_L99mm_D36mm_P1270mm_Horizontal_60125817
R3_R_Axial_DIN0411_L99mm_D36mm_P1270mm_Horizontal_6012582E
R4_R_Axial_DIN0411_L99mm_D36mm_P1270mm_Horizontal_60125845
R5_R_Axial_DIN0411_L99mm_D36mm_P1270mm_Horizontal_6012585C
R6_R_Axial_DIN0411_L99mm_D36mm_P1270mm_Horizontal_60125873
R7_R_Axial_DIN0411_L99mm_D36mm_P1270mm_Horizontal_6012588A
R8_R_Axial_DIN0411_L99mm_D36mm_P1270mm_Horizontal_601258A1
R9_R_Axial_DIN0411_L99mm_D36mm_P1270mm_Horizontal_601258B8
R10_R_Axial_DIN0411_L99mm_D36mm_P1270mm_Horizontal_601258CF
R11_R_Axial_DIN0411_L99mm_D36mm_P1270mm_Horizontal_601258E6
R12_R_Axial_DIN0411_L99mm_D36mm_P1270mm_Horizontal_601258FD
R13_R_Axial_DIN0411_L99mm_D36mm_P1270mm_Horizontal_60125914
R14_R_Axial_DIN0411_L99mm_D36mm_P1270mm_Horizontal_6012592B
U1_DIP-8_W7.62mm_60125BCB
U2_DIP-8_W7.62mm_60125BE7
Q3_TO-92L_Inline_Wide_6012A555
Q4_TO-92L_Inline_Wide_6012A569
Q5_TO-92L_Inline_Wide_6012A57D
Q6_TO-92L_Inline_Wide_6012A591
R15_R_Axial_DIN0411_L99mm_D36mm_P1270mm_Horizontal_60190BF0
R16_R_Axial_DIN0411_L99mm_D36mm_P1270mm_Horizontal_60190C07
U5_TO_220_5_Pentawatt_Multiwatt_5_Vertical_StaggeredType1_60190C2D

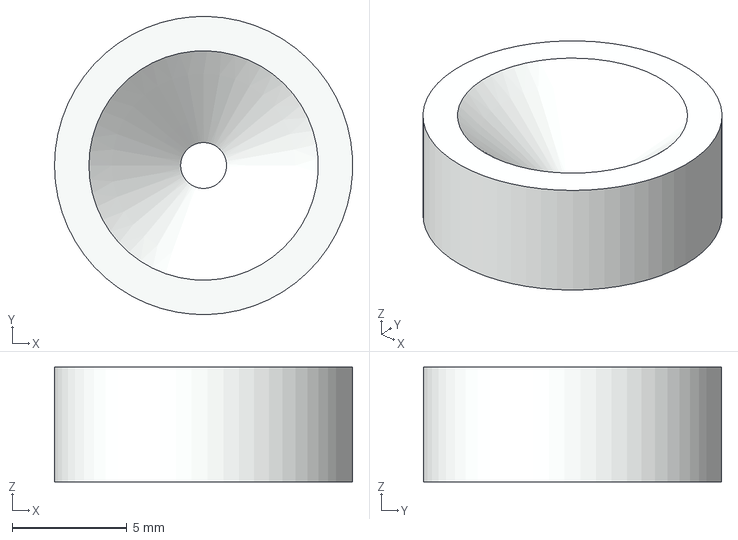
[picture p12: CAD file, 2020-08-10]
hardware/mechanics/freeCad_conversion/nozzle_big.step
13.0 x 13.0 x 5.00 mm

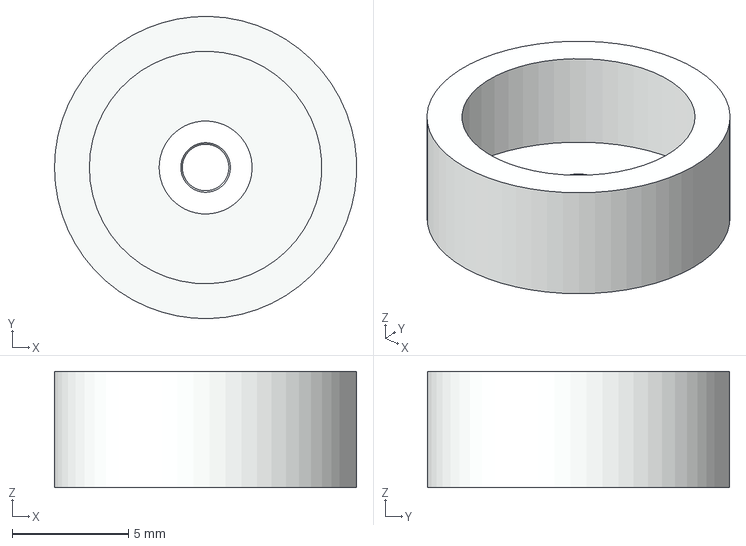
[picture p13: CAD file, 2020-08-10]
hardware/mechanics/from_raiser_et_al/nozzle_big_ipt/0006.step
13.0 x 13.0 x 5.00 mm

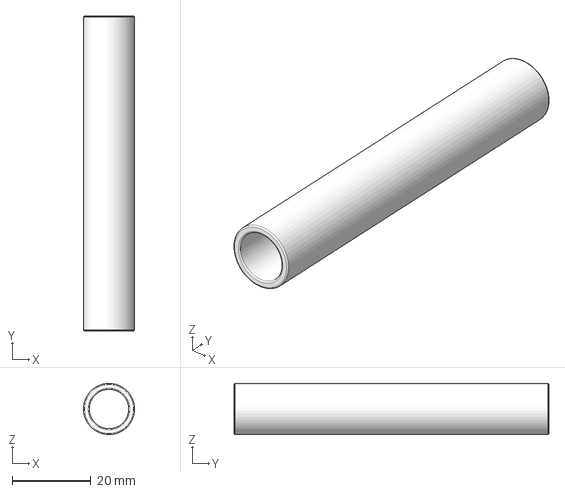
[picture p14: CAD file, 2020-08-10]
hardware/mechanics/from_raiser_et_al/tube_long_ipt/0008.step
13.0 x 80.0 x 13.0 mm

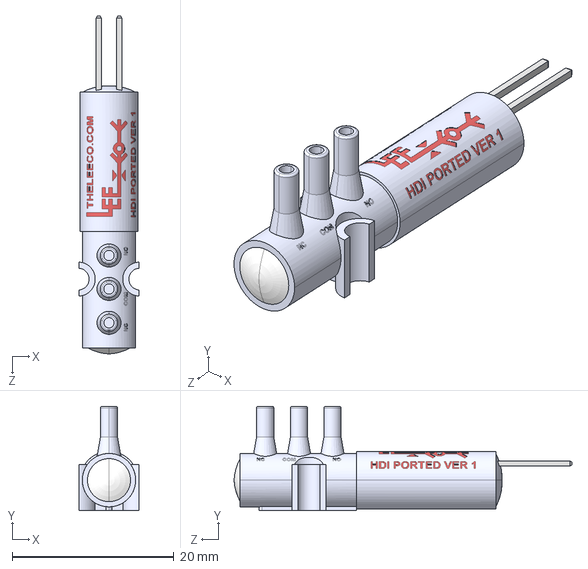
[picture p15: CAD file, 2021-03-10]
hardware/mechanics/new_system/LHDA3D00006AA - PRTD - 3Way,2Way - V1.step
7.47 x 12.9 x 41.8 mm

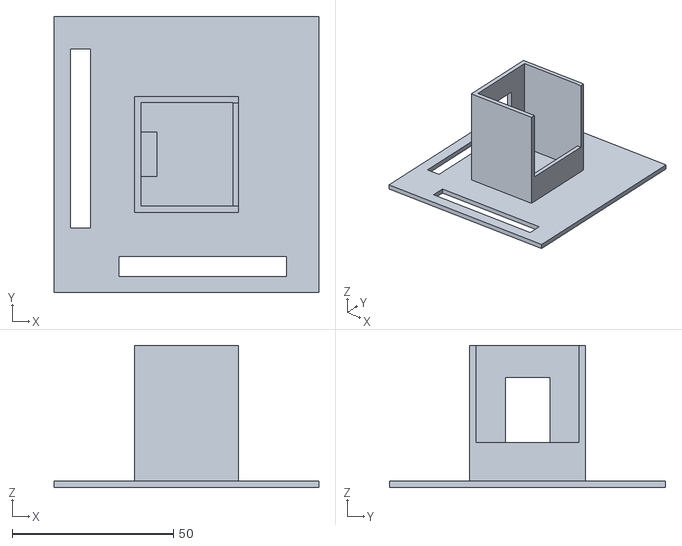
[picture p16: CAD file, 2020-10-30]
hardware/mechanics/printed_holders/rotameter.stl
81.9 x 85.5 x 44.0

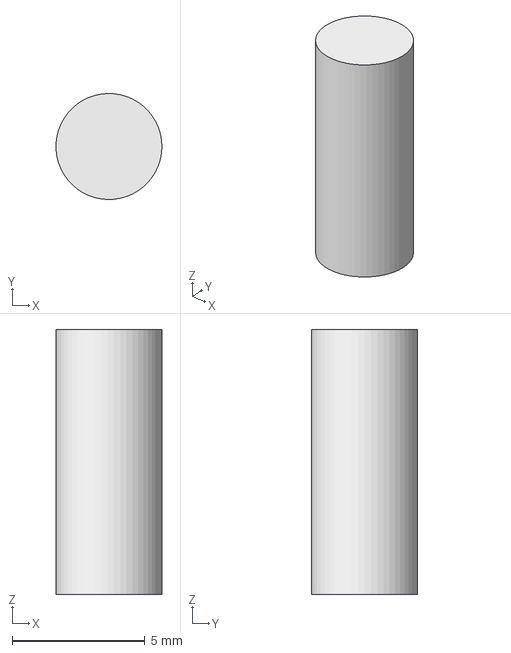
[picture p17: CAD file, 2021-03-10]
hardware/mechanics/test/test.FCStd
4.00 x 4.00 x 10.0 mm

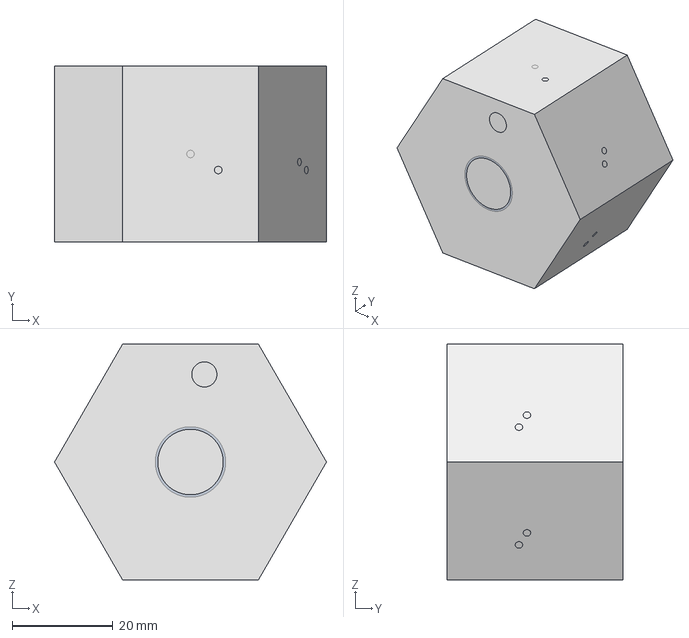
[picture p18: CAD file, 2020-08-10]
hardware/mechanics/from_raiser_et_al/test.step
54.0 x 35.0 x 46.8 mm

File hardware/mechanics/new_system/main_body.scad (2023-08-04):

//cc = centralchamber
ccDia = 5;
ccLen = 5;
ccExitDia = 2;
ccExitLen = 2;

glass1Dia = 7.95;
glass1DiaRim = glass1Dia+4;
glass1Len = 20;
glass2Dia = 7;
glass2Len = 20;

blockDia = 25;
blockLen = 40;

longChanLen = 20;//15;
longChanDia = 2.9+0.1;

shortChanLen = 8;//valve protusions are 6.33mm
centralChanLen = blockDia/2+1;

valveFitDia = 2;//2.03;
interValveDis = 4.19;

blockHolderx = 20;
blockHoldery = blockDia/2;
blockHolderz = 10;

tol = 0.1;
$fn = 60;

////////modules//////////////////////////

module central_chamber(){
//central part of the chamber
cylinder(d=ccDia+2*tol,h=ccLen);

//exit bottom
translate([0,0,-ccExitLen]){
cylinder(d2=ccDia+2*tol,d1=ccExitDia+2*tol,h=ccExitLen);}

translate([0,0,-2*ccExitLen]){
cylinder(d1=glass2Dia+2*tol,d2=ccExitDia+2*tol,h=ccExitLen);
    }//end translate

translate([0,0,-2*ccExitLen-glass2Len]){
cylinder(d1=glass2Dia+2*tol,d2=glass2Dia+2*tol,h=glass2Len);
    }//end translate

//exit top
union(){
translate([0,0,ccLen]){
cylinder(d1=ccDia+2*tol,d2=ccExitDia+2*tol,h=ccExitLen);}

translate([0,0,ccLen+ccExitLen]){
cylinder(d2=glass1Dia+2*tol,d1=ccExitDia+2*tol,h=ccExitLen);
    }//end translate
}//end union

translate([0,0,ccLen+2*ccExitLen]){
cylinder(d2=glass1Dia+2*tol,d1=glass1Dia+2*tol,h=glass1Len);
    }//end translate

}//end module






module valve_fit2(){

////////////// valve entries ////////////////////////////////////////
    rotate([0,0,45]){
    union(){
    for (i=[0:1:2]){
       
            if (i==0){
                cylinder(d=valveFitDia+2*tol,h=centralChanLen,center=true);
            }//end if
            else{
                translate([interValveDis*i,0,-(centralChanLen-shortChanLen)/2]){
                    cylinder(d=valveFitDia+2*tol,h=shortChanLen,center=true);
                    }//end translate
                }//end else
    
        }//end for
    }//end union
}//end rotate
/////////////////// tubing entries ///////////////////////////
    rotate([90,0,0]){
    union(){
    //for (i=[2:2]){    
    //    translate([i*interValveDis*sin(45),0,-i*interValveDis*sin(45)+(valveFitDia/2-longChanLen)/2]){
    //        cylinder(d=valveFitDia+2*tol,h=longChanLen,center=true);
    //        }//end translate

    //    }//end for
        rotate([-5,2.5,0]){
        translate([interValveDis*sin(47.5),0,(-interValveDis-longChanLen/2)*sin(47.5)-1]){
            cylinder(d1=valveFitDia+2*tol,d2=valveFitDia+2*tol,h=longChanLen-4,center=true);
            }//end translate
            
        }//rotate
        
        rotate([-5,2.5,0]){
        translate([interValveDis*sin(47.5),0,(-interValveDis-longChanLen/2)*sin(47.5)-7]){
            cylinder(d1=longChanDia+2*tol,d2=longChanDia+2*tol,h=longChanLen,center=true);
            }//end translate
            
        }//rotate

        rotate([-5,-5,0]){
        translate([2*interValveDis*sin(40),0,(-longChanLen-2*interValveDis)*sin(40)+2.5]){
            cylinder(d1=valveFitDia+2*tol,d2=valveFitDia+2*tol,h=longChanLen-11,center=true);
            }//end translate
            
        }//rotate
        
                rotate([-5,-5,0]){
        translate([2*interValveDis*sin(40),0,(-longChanLen-2*interValveDis)*sin(40)-5]){
            cylinder(d1=longChanDia+2*tol,d2=longChanDia+2*tol,h=longChanLen,center=true);
            }//end translate
            
        }//rotate
        
        
    }//end union 
}//end rotate

}// end module





////////////////////////////////////////////

difference(){ 
    union(){
    translate([-blockDia/2,-blockDia/2,-5]){
    cube([blockDia,blockDia, blockLen]);
    }//end translate
    translate([0,0,-(glass1Len)/2]){
    cylinder(d=glass1DiaRim,h=20);
    }//end translate
    
    //block holder
    translate([blockDia/2,0,blockLen-blockHolderz-5]){
    cube([blockHolderx,blockHoldery,blockHolderz]);
    }//end translate
}//end union

    translate([0,0,12]){
    central_chamber();
    }//end translate



translate([0,5,14]){
    rotate([90,0,0]){
    union(){    
    translate([0,0,-0.9]){
    valve_fit2();
    }

    translate([00,0,blockDia/2-1.7]){
        rotate([180,0,180]){
        valve_fit2();
        }//end rotate
    }//end translate

    translate([shortChanLen-2,-0,5]){
        rotate([0,-90,0]){
        valve_fit2();
        }//end rotate
    }//end translate

    translate([-shortChanLen+2.1,-0,5]){
        rotate([0,90,0]){
        valve_fit2();
        }//end rotate
    }//end translate

}//end union

}//end rotate
}//end translate


//translate([-3.8,-blockDia/2-1,-15]){
//    cube([blockDia+10,blockDia+2,blockLen+15]);
//    }//end translate



}//end difference



//valve_fit2();



//////////////// legacy /////////////////////////


/*
module valve_fit(tubes=0){

    cylinder(d=valveFitDia+2*tol,h=centralChanLen,center=true);

    translate([interValveDis,0,-(centralChanLen-shortChanLen)/2]){
        
        cylinder(d=valveFitDia+2*tol,h=shortChanLen,center=true);
        rotate([90,0,0]){
            if(tubes==1){
                translate([0,(shortChanLen-valveFitDia)/2,-blockLen-0]){
                tubing(d1 = longChanDia, d2=longChanDia-1+2*tol);
                }//end translate
                }//end if
            translate([0,(shortChanLen-valveFitDia)/2,-longChanLen/2+valveFitDia/10]){
                
                cylinder(d=longChanDia+2*tol,h=longChanLen,center=true);
            }//end translate
        }//end rotate
    }//end translate

translate([2*interValveDis,0,-(centralChanLen-shortChanLen)/2]){
    cylinder(d=valveFitDia+2*tol,h=shortChanLen,center=true);
    rotate([-90,0,0]){
        translate([0,-(shortChanLen-valveFitDia)/2,longChanLen/2-valveFitDia/10]){
            cylinder(d=longChanDia+2*tol,h=longChanLen,center=true);
        }//end translate
    }//end rotate
    
}//end translate

}// end module


module tubing(d1 = 5, d2 = 3, he= 10){
    difference(){
    cylinder(d = d1,h=he);
        translate([0,0,-0.5]){
            cylinder(d = d2, h = he +1);
        }//end translate
        }//end difference
    }//end module tubing

*/

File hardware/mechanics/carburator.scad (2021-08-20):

tubeD = 10;
sectionL = 15;
$fn=30;
tol=0.1;
difference(){
    translate([0,0,2.5]){
%cylinder(d=tubeD+10,h=4*sectionL-5);
    }
union(){
cylinder(d=tubeD,h=sectionL);

translate([0,0,sectionL]){
cylinder(d1=tubeD,d2=2,h=sectionL);
    }
    
translate([0,0,2*sectionL]){
cylinder(d1=2,d2=tubeD,h=sectionL);
    }
    
translate([0,0,3*sectionL]){
cylinder(d=tubeD,h=sectionL);
    }


translate([-0.5,0,2*sectionL]){
    rotate([0,90,0]){    
        cylinder(d=1,h=30);
    }//end rotate
    }//end translate

}//end union
}//end difference


cylinder(d=tubeD-2*tol,h=4);

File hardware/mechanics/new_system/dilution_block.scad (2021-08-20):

tubeD = 2;
tubeH = 10;

valveFitDia = 2;//2.03;
interValveDis = 4.19;

blockDia = 80;
blockLen = 40;

shortChanLen = 8;//valve protusions are 6.33mm
centralChanLen = blockDia/2+1;
exitLen=20;



tol = 0.1;




$fn =20;


module valve_fit(){
   
    for (i=[0:1:2]){
        if (i==0){
            cylinder(d=valveFitDia+2*tol,h=centralChanLen);
            translate([0,0,centralChanLen-valveFitDia/2]){
        rotate([90,0,0]){
        cylinder(d=valveFitDia+2*tol,h=centralChanLen);
        }//end rotate
         }//end translate   
            }//end if
        else{
            translate([interValveDis*i,0,0]){
                cylinder(d=valveFitDia+2*tol,h=shortChanLen);
                }//end translate
                translate([interValveDis*i,0,shortChanLen-valveFitDia/2]){
        rotate([45,180,0]){
        cylinder(d=valveFitDia+2*tol,h=exitLen);
        }//end rotate
    }//end transalte
            }//end else
        }//end for
        
    
}// end module
/*

cylinder(d=tubeD+5,h=tubeH);



for (i = [0:36:360]){
    translate([0,0,tubeH-1]){
    rotate([0,45,i]){
    cylinder(d=tubeD,h=tubeH*3);
    }//end rotate
}//end translate

}//end for

*/


module main_body(){
    cylinder(d=10,h=100);
    for (i = [5:10:100]){
        translate([0,0,i]){
    rotate([0,90,0]){
    cylinder(d=tubeD,h=tubeH*3);
    }
}
        }
    
    }//end module
    
//difference(){
translate([0,-25,0]){
rotate([90,-10,0]){
    cylinder(d1=65,d2=55,h=5,$fn=10);
}
}
    

   for (i = [0:36:360]){ 
    rotate([-45,i,0]){
        translate([0,-0,-centralChanLen+valveFitDia/2]){

         valve_fit();
        }
    }
}
//}//end difference

//valve_fit();

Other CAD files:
hardware/mechanics/from_raiser_et_al/nozzle_big.FCStd
hardware/mechanics/freeCad_conversion/test2.stl
hardware/mechanics/new_system/v0.1/pre-flush.FCStd
hardware/mechanics/printed_holders/rotameter_n_digital_pressure_holders.stl
hardware/mechanics/new_system/flow_to_tube_connectors.scad
hardware/mechanics/freeCad_conversion/body.FCStd
hardware/mechanics/freeCad_conversion/body.amf
hardware/mechanics/freeCad_conversion/body.step
hardware/mechanics/freeCad_conversion/body_cutout.FCStd
hardware/mechanics/freeCad_conversion/body_step.FCStd
hardware/mechanics/freeCad_conversion/holder.FCStd
hardware/mechanics/freeCad_conversion/nozzle_big.FCStd
hardware/mechanics/freeCad_conversion/nozzle_small.FCStd
hardware/mechanics/freeCad_conversion/rod.FCStd
hardware/mechanics/freeCad_conversion/test3.amf
hardware/mechanics/freeCad_conversion/tube.FCStd
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

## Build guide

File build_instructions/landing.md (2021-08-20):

# Odour Stimulator

[BOM]:parts.yaml

Welcome to the building and using instructions for odour stimulator.

To build this system, we suggest collating all the necessary parts necessary to build this system, so that you can spend time with ordering only once. 

* [.](electronics.md){step: True}
* [.](mechanics.md){step: True}

### Skills needed:
- Soldering 
- Using power tools (drill)
- Using hand tools (screwdriver, wrench)
- Programming (or at least following online tutorials on how to upload code to microccontrollers)

{{BOM}}

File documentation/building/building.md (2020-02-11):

**Use this folder to create files for building instructions:**
- Each equipment is going to have a different building process, but here are some suggestions on how to organise things:

<br>

1. getting started:
 - a brief overview of the equipment people are about to build and what kind of knowledge they are expected to have (soldering, programming). Also, is this safe for amateurs/kids? Is it a one person build? How much time does it take on average to build it?
 - Could you add contact information (email, forum, twitter handle) for people to reach out in case something goes wrong?

<br>

2. List of materials needed:
 - In the form of a table, containing part name, quantity and a couple of words on what they do. Extra points if the parts are divided according to the building steps (below)
 - Remember to include the tools necessary as well! (pliers, saw, computer, etc)  

 |part name| function  | quantity  | build step  | obs.  |
 |---|---|---|---|---|
 |LM2596| voltage regulator  | 2  | 3  | these could be substituted by XX  |
 | Nose needle Pliers  | hold components while soldering  | 1  | all steps  | regular pliers would also work  |

<br>

3. build steps:
 - Divide this section in as many subparts as you like and try to be as clear as possible. Would someone seeing the whole thing for the first time be able to build it? (it is a good exercise to oversee someone building the equipment using only your written/video/figure instructions)
 - Is a video a better way to instruct people how to use it? try to keep the file size as small as possible without compromising quality. Also reach out to us, as a good idea might be to create a different repository for the video files.  

<br>

4. Last checks before powering up/using for the first time:
 - Could people do one more check of everything before powering up things? Maybe double check that the capacitors were soldered in the proper orientation? Make sure there are no cut metal parts shorting the bottom side of the PCB? Make sure the area around the equipment is clear and won't be hit if the equipment has moving parts (eg shakers, centrifuges, etc).

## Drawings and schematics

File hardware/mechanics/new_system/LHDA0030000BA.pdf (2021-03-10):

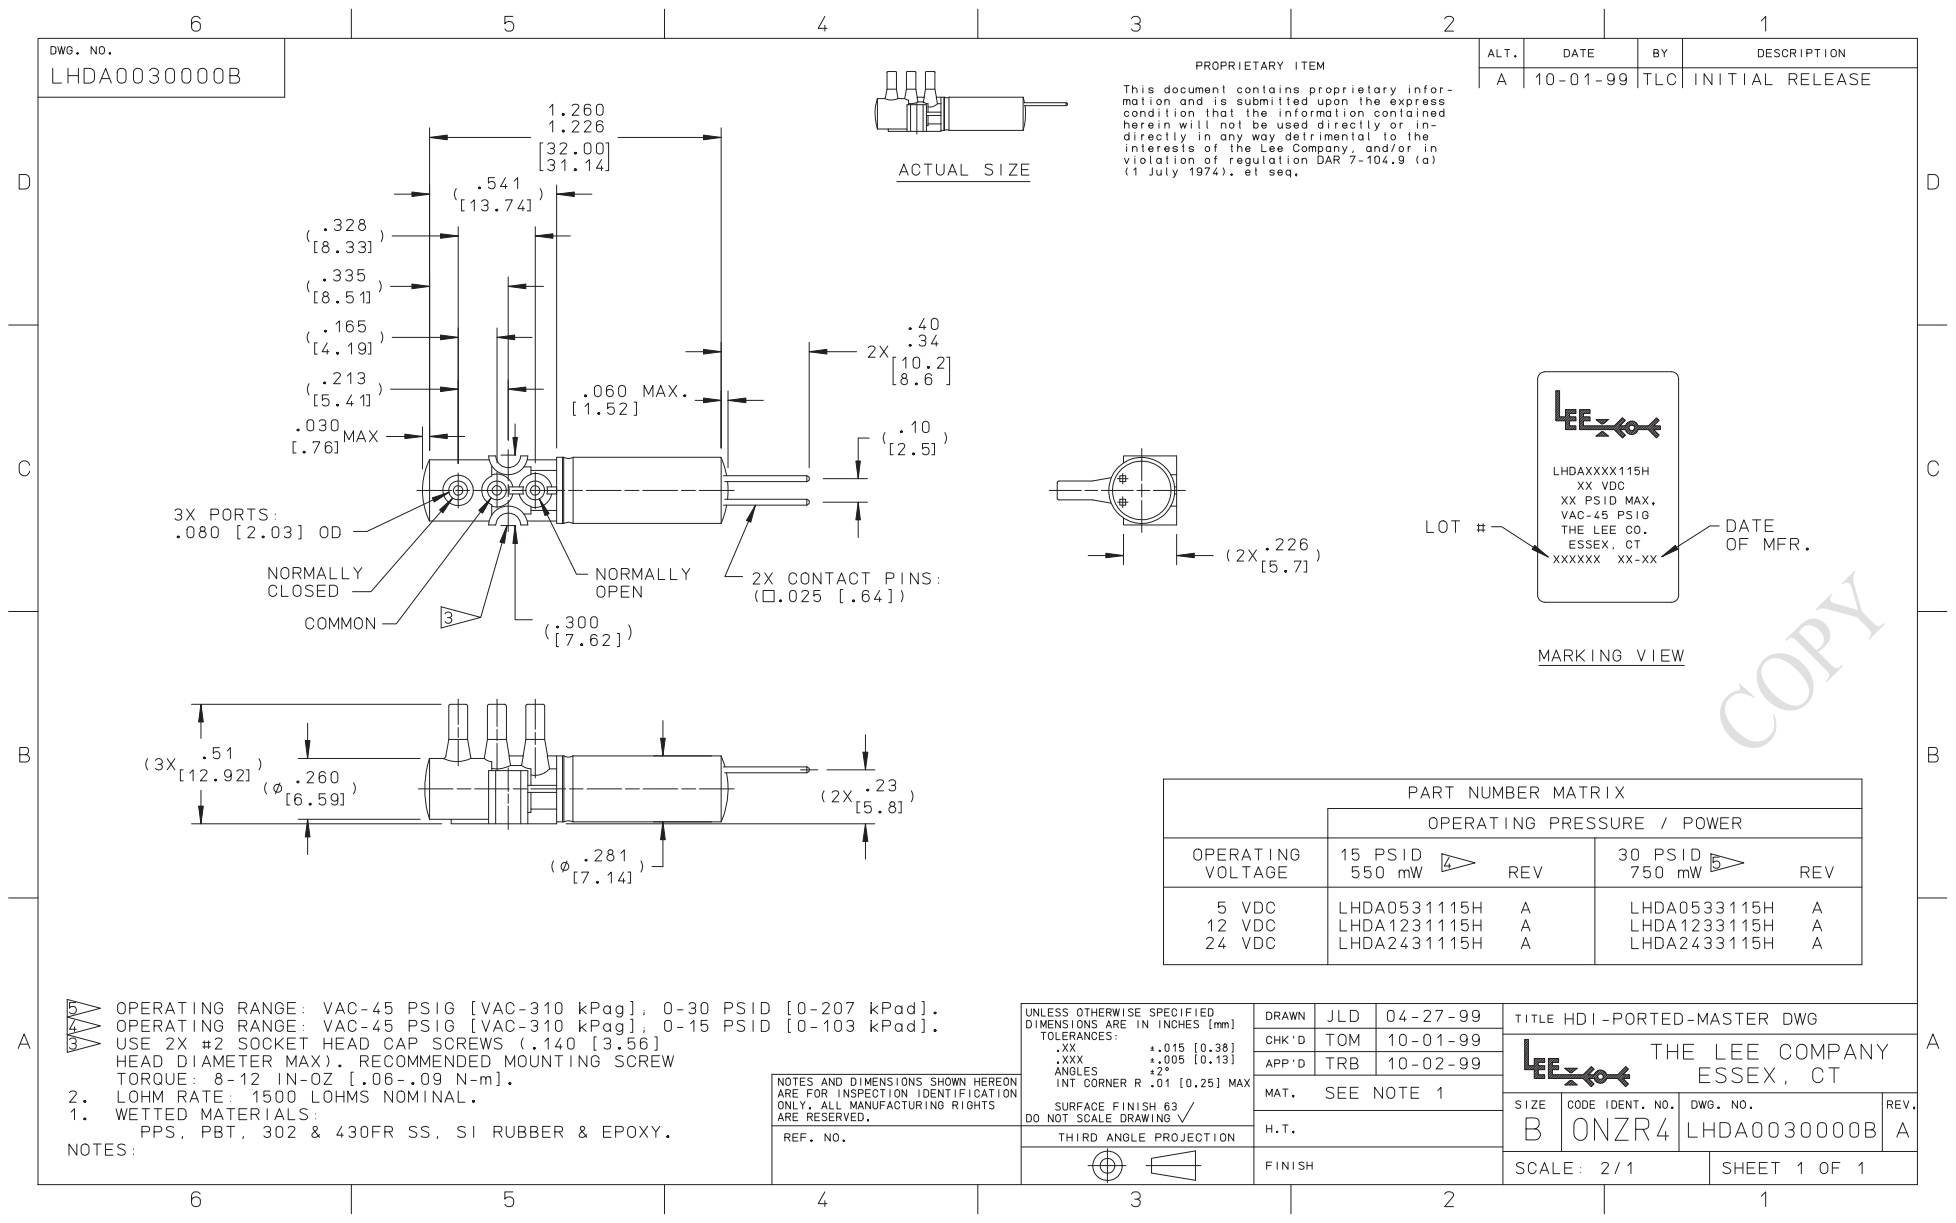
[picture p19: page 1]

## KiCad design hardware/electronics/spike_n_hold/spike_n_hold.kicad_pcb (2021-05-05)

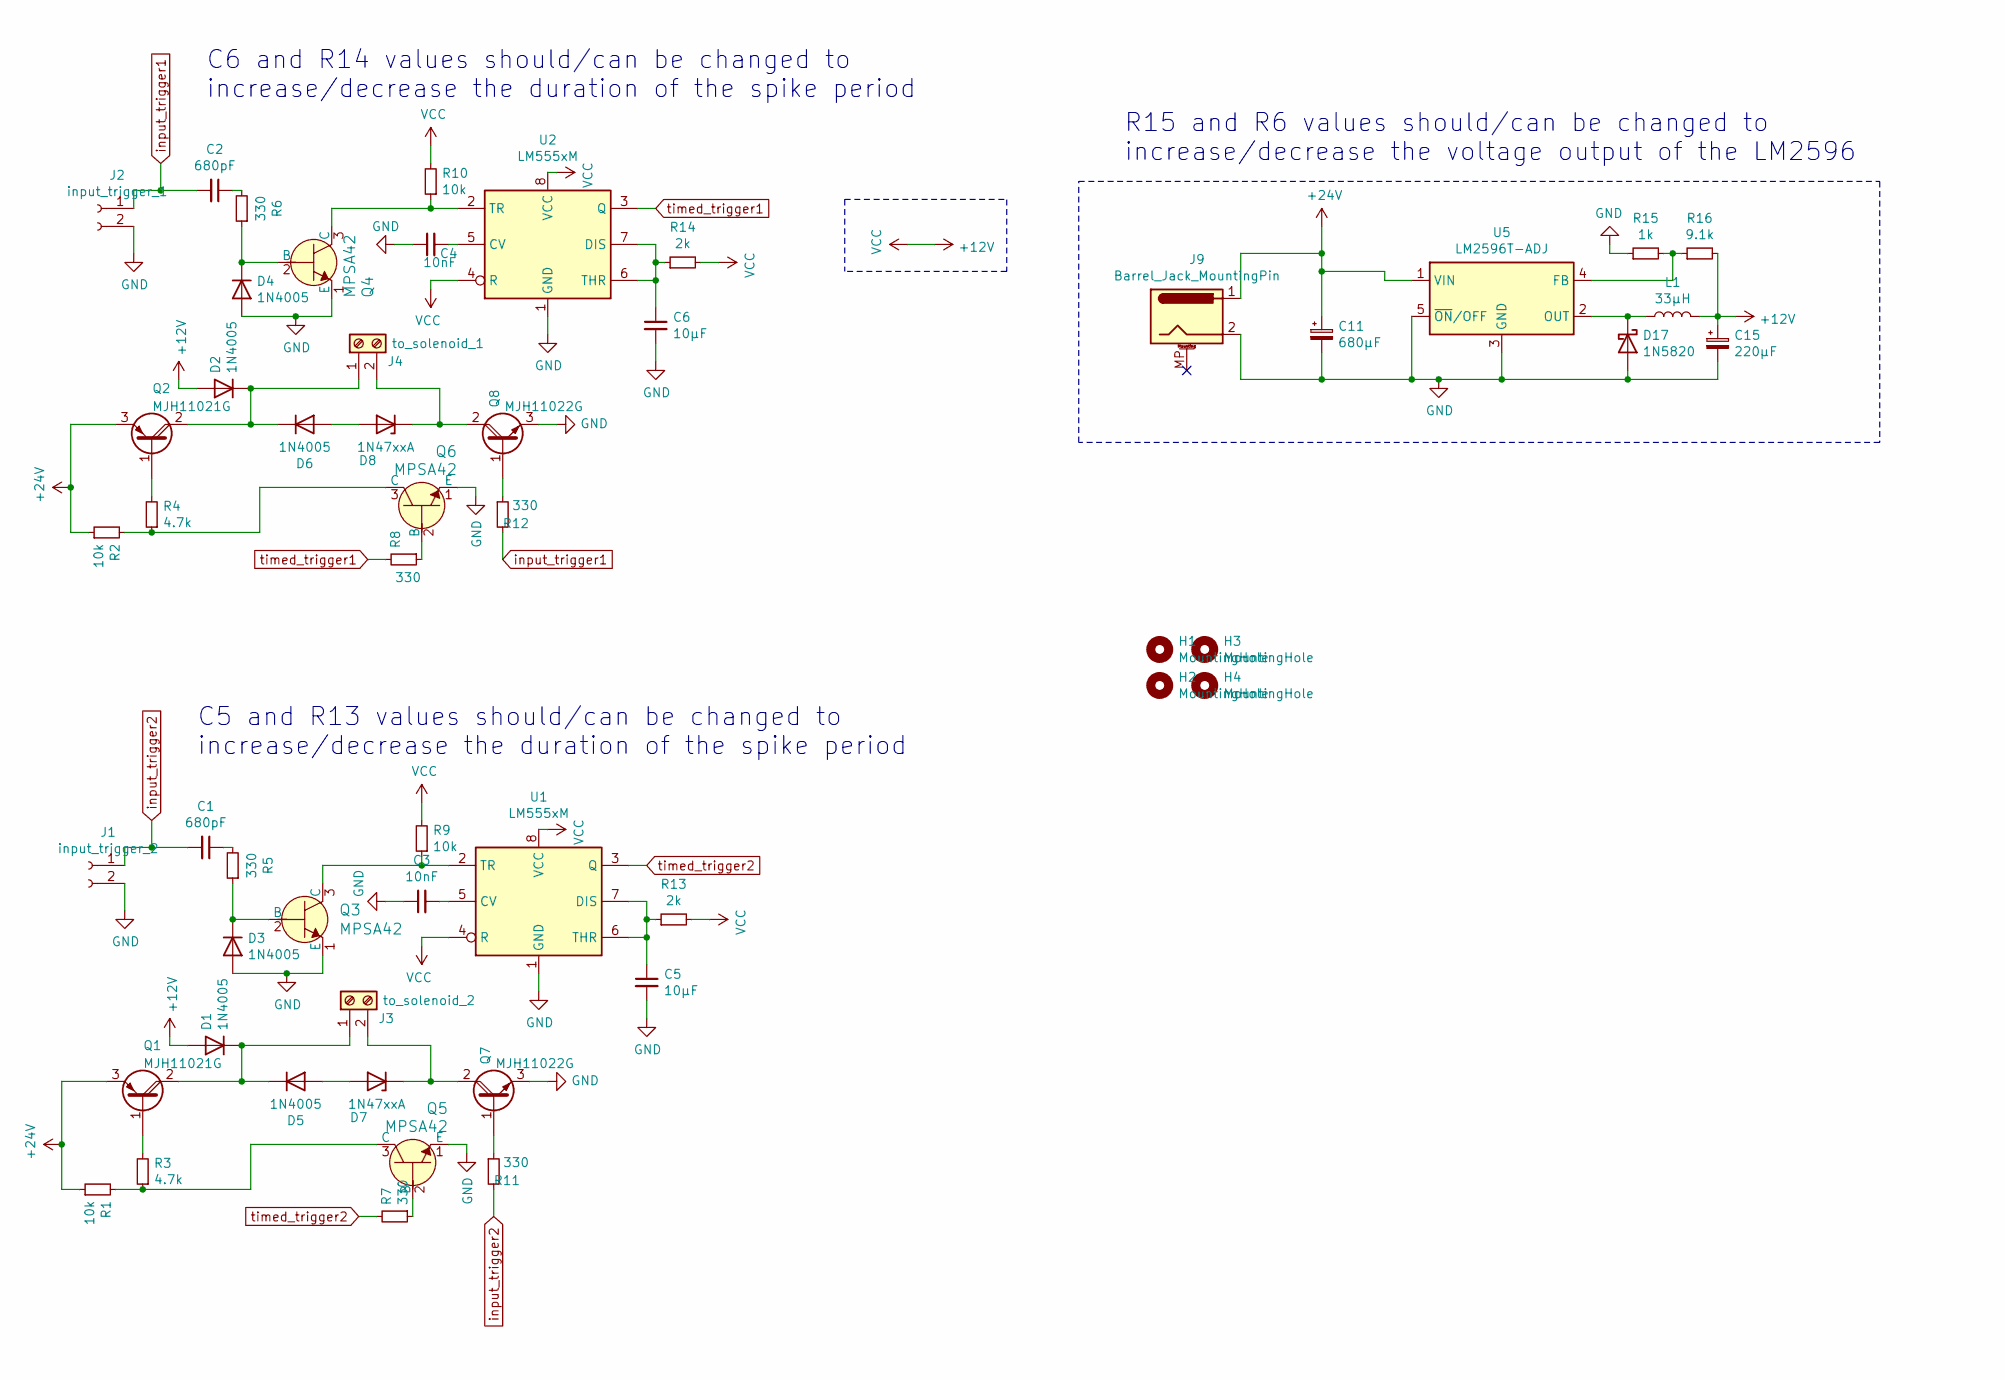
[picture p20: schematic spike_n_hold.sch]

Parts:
C1, C2: 680pF; C_Disc_D5.1mm_W3.2mm_P5.00mm
C3, C4: 10nF; C_Disc_D5.1mm_W3.2mm_P5.00mm
C5, C6: 10µF; C_Disc_D5.1mm_W3.2mm_P5.00mm
C11: 680µF; CP_Radial_D10.0mm_P5.00mm
C15: 220µF; CP_Radial_D10.0mm_P5.00mm
D1, D2, D3, D4, D5, D6: 1N4005; D_DO-41_SOD81_P10.16mm_Horizontal
D7, D8: 1N47xxA; D_DO-41_SOD81_P10.16mm_Horizontal
D17: 1N5820; D_DO-201AD_P15.24mm_Horizontal
H1, H2, H3, H4: MountingHole; MountingHole_3.2mm_M3
J1: input_trigger_2; PinHeader_1x02_P2.54mm_Vertical
J2: input_trigger_1; PinHeader_1x02_P2.54mm_Vertical
J3: to_solenoid_2; PinHeader_1x02_P2.54mm_Vertical
J4: to_solenoid_1; PinHeader_1x02_P2.54mm_Vertical
J9: Barrel_Jack_MountingPin; Barrel_Jack_5.5mmODx2.1mmID_PJ-202A
L1: 33µH; L_Radial_D7.5mm_P3.50mm_Fastron_07P
Q1, Q2: MJH11021G; TO-247-3_Vertical
Q3, Q4, Q5, Q6: MPSA42; TO-92L_Inline_Wide; MPN MPSA42; Digi-Key_PN MPSA42FS-ND
Q7, Q8: MJH11022G; TO-247-3_Vertical
R1, R2, R9, R10: 10k; R_Axial_DIN0411_L9.9mm_D3.6mm_P12.70mm_Horizontal
R3, R4: 4.7k; R_Axial_DIN0411_L9.9mm_D3.6mm_P12.70mm_Horizontal
R5, R6, R7, R8, R11, R12: 330; R_Axial_DIN0411_L9.9mm_D3.6mm_P12.70mm_Horizontal
R13, R14: 2k; R_Axial_DIN0411_L9.9mm_D3.6mm_P12.70mm_Horizontal
R15: 1k; R_Axial_DIN0411_L9.9mm_D3.6mm_P12.70mm_Horizontal
R16: 9.1k; R_Axial_DIN0411_L9.9mm_D3.6mm_P12.70mm_Horizontal
U1, U2: LM555xM; DIP-8_W7.62mm_LongPads
U5: LM2596T-ADJ; TO-220-5_P3.4x3.7mm_StaggerOdd_Lead3.8mm_Vertical

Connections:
+12V: C15.1, D1.2 (A), D2.2 (A), L1.2, R9.2, R10.2, R13.2, R14.2, R16.2, U1.4 (R), U1.8 (VCC), U2.4 (R), U2.8 (VCC)
+24V: C11.1, J9.1, Q1.3 (E), Q2.3 (E), R1.1, R2.1, U5.1 (VIN)
GND: C3.1, C4.1, C5.2, C6.2, C11.2, C15.2, D3.2 (A), D4.2 (A), D17.2 (A), J1.2, J2.2, J9.2, Q3.1 (E), Q4.1 (E), Q5.1 (E), Q6.1 (E), Q7.3 (E), Q8.3 (E), R15.1, U1.1 (GND), U2.1 (GND), U5.3 (GND), U5.5 (~ON~/OFF)
unnamed: C1.1, R5.2
unnamed: C2.1, R6.2
unnamed: C3.2, U1.5 (CV)
unnamed: C4.2, U2.5 (CV)
unnamed: C5.1, R13.1, U1.6 (THR), U1.7 (DIS)
unnamed: C6.1, R14.1, U2.6 (THR), U2.7 (DIS)
unnamed: D1.1 (K), D5.1 (K), J3.1, Q1.2 (C)
unnamed: D2.1 (K), D6.1 (K), J4.1, Q2.2 (C)
unnamed: D3.1 (K), Q3.2 (B), R5.1
unnamed: D4.1 (K), Q4.2 (B), R6.1
unnamed: D5.2 (A), D7.2 (A)
unnamed: D6.2 (A), D8.2 (A)
unnamed: D7.1 (K), J3.2, Q7.2 (C)
unnamed: D8.1 (K), J4.2, Q8.2 (C)
unnamed: D17.1 (K), L1.1, U5.2 (OUT)
unnamed: Q1.1 (B), R3.2
unnamed: Q2.1 (B), R4.2
unnamed: Q3.3 (C), R9.1, U1.2 (TR)
unnamed: Q4.3 (C), R10.1, U2.2 (TR)
unnamed: Q5.2 (B), R7.1
unnamed: Q5.3 (C), R1.2, R3.1
unnamed: Q6.2 (B), R8.1
unnamed: Q6.3 (C), R2.2, R4.1
unnamed: Q7.1 (B), R11.1
unnamed: Q8.1 (B), R12.1
unnamed: R15.2, R16.1, U5.4 (FB)
input_trigger1: C2.2, J2.1, R12.2
input_trigger2: C1.2, J1.1, R11.2
timed_trigger1: R8.2, U2.3 (Q)
timed_trigger2: R7.2, U1.3 (Q)

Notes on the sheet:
C6 and R14 values should/can be changed to increase/decrease the duration of the spike period
C5 and R13 values should/can be changed to increase/decrease the duration of the spike period
R15 and R6 values should/can be changed to increase/decrease the voltage output of the LM2596

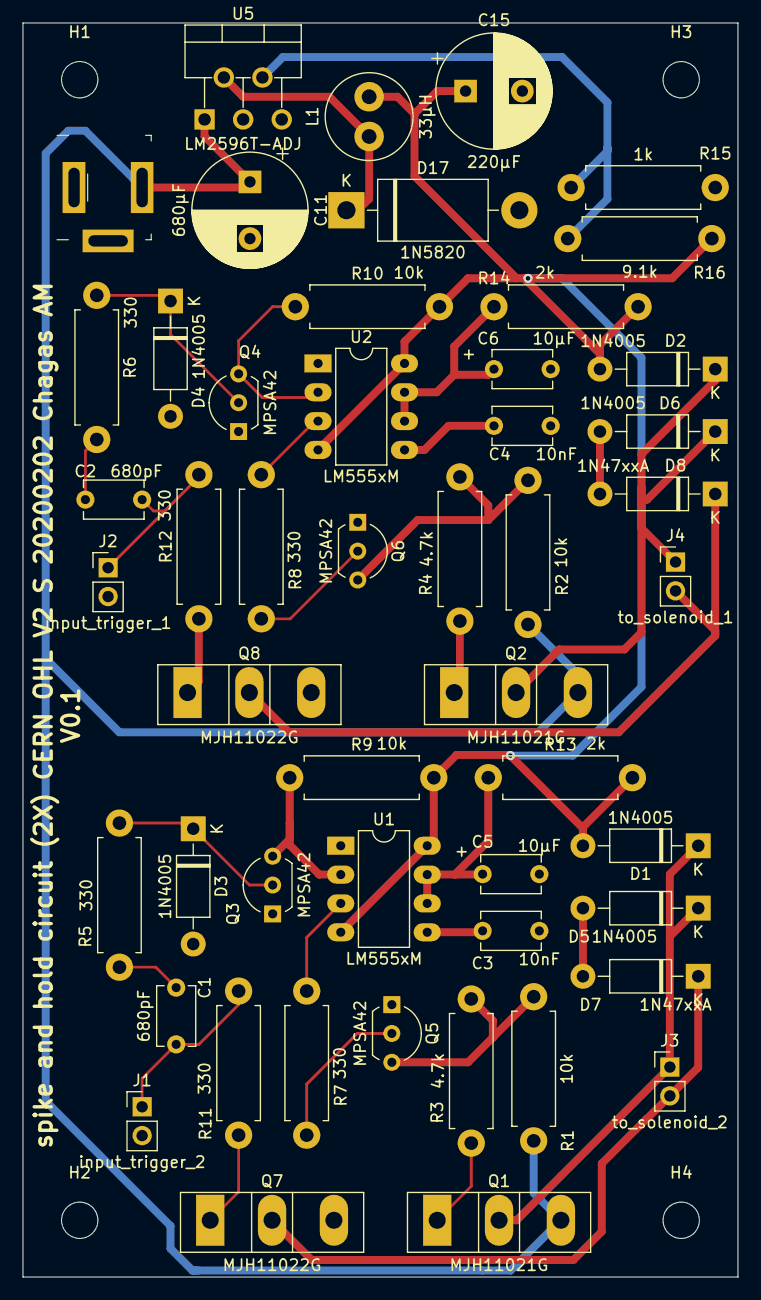
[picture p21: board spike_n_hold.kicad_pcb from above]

Board: 2 copper layers, 63.0 x 110.5 mm, 54 parts (0 on the bottom side), 33 nets.

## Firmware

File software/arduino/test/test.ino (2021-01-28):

#include <SerialCommand.h>

int temp = 0;
int flush1 = 19;
int main1 = 18;
int relieve1 = 21;
int trigger1 = 12;
int trigger2 = 13;
int incoming = 0;


SerialCommand sCmd;     // The demo SerialCommand object

void setup() {
  Serial.begin(115200);
  pinMode(2,OUTPUT);
  pinMode(flush1,OUTPUT);
  pinMode(main1,OUTPUT);
  pinMode(relieve1,OUTPUT);
  pinMode(trigger1,OUTPUT);
  pinMode(trigger2,OUTPUT);
  
  sCmd.addCommand("f11",    flush1_on);
  sCmd.addCommand("f10",    flush1_off);
  sCmd.addCommand("m11",    main1_on);
  sCmd.addCommand("m10",    main1_off);
  sCmd.addCommand("r11",    relieve1_on);
  sCmd.addCommand("r10",    relieve1_off);
  sCmd.addCommand("p1",    prot1);
  
  
}

void loop() {
  //if (Serial.available() > 0) {
  //  // read the incoming byte:
  //  incoming = Serial.read();
  //  temp = incoming - '0';
  // Serial.println(temp==1);
  //  Serial.println(atoi(incoming));
  //  }// end if

  //if (temp == 1){
  //  temp=0;
  sCmd.readSerial();     // We don't do much, just process serial commands

}

//callbacks

void prot1(){
  Serial.println("protocol1");  
  digitalWrite(2,HIGH);
  digitalWrite(flush1,HIGH);
  digitalWrite(trigger1,HIGH);

  delay(5000);
  digitalWrite(2,LOW);
  digitalWrite(trigger2,HIGH);
  digitalWrite(main1, HIGH);
  digitalWrite(relieve1, HIGH);
  delay(1000);
  digitalWrite(trigger1,LOW);
  digitalWrite(trigger2,LOW);
  digitalWrite(flush1, LOW);
  digitalWrite(main1, LOW);
  digitalWrite(relieve1, LOW);
  }

void flush1_on(){
  Serial.println("flush1 on");  

  digitalWrite(flush1,HIGH);
  digitalWrite(trigger1,HIGH);
  
  }

void flush1_off(){
  Serial.println("flush1 off");  

  digitalWrite(flush1,LOW);
  digitalWrite(trigger1,LOW);
  }

 void main1_on(){
  Serial.println("main1 on");  

  digitalWrite(main1,HIGH);
  digitalWrite(trigger2,HIGH);
  }

 void main1_off(){
  Serial.println("main1 off");  
  digitalWrite(trigger2,LOW);

  digitalWrite(main1,LOW);
  }

 void relieve1_on(){
  Serial.println("relieve1 on");  

  digitalWrite(relieve1,HIGH);
  }
  
 void relieve1_off(){
  Serial.println("relieve1 off");  

  digitalWrite(relieve1,LOW);
  }

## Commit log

2020-02-11 initial clean up and uploading files
    [Assembly.iam, body.ipt, holder.ipt, nozzle_big.ipt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]
2020-02-11 clean up bill of materials. Splitting it into electronics and mechanics for now
2020-02-12 converted all autodesk inventor to files readable in freecad
    [body.FCStd, body.step, body_step.FCStd, holder.FCStd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]
2020-02-17 created bill of materials for mechanical parts as well as gcode and amf files for central body
    [body.amf]
2020-02-27 prepare gcode for printing with PP
    [body.FCStd, body.amf, body_step.FCStd, holder.FCStd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]
2020-03-06 gcode for printing
2020-08-04 update to 3D printed parts and readme
    [body v1.iges, body.FCStd, body.step, body_cutout.FCStd]
2020-08-10 revamp mechanical parts for printing and update readme
    [0006.step, 0008.step, body v1.iges, body.FCStd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]
2020-10-29 initial design for rotameter holder
    [M6 Hex Socket Cap Screw 30mm.step, rotameter_n_digital_pressure_holders.scad]
2020-10-29 add stl file
    [rotameter_n_digital_pressure_holders.scad, rotameter_n_digital_pressure_holders.stl]
2020-10-29 both models
    [rotameter_n_digital_pressure_holders.scad, rotameter_n_digital_pressure_holders.stl]
2020-10-30 add individual STLs and tweak design
    [digital_pressure_holder.stl, rotameter.stl, rotameter_n_digital_pressure_holders.scad]
2021-01-13 schematics of the spike and hold circuitry
    [spike_n_hold.kicad_pcb, spike_n_hold.sch]
2021-01-13 update mechanics
    [main_body.stl, pre-flush.FCStd, pre-flush.stl]
2021-01-13 fix capacitor value
    [spike_n_hold.sch]
2021-01-28 last implementation of the 6 spike and trigger board.
    [1-click-bom.tsv, DIGIKEY_BOM_TEMP.csv, spike_n_hold.sch]
2021-01-28 reimplementation, 2 modules per board, as they are equivalent to one odour channel, or one dilution step
    [spike_n_hold.kicad_pcb, spike_n_hold.sch]
2021-03-01 central body measurements and luer fitting print test
    [main_halved_for_measurements.FCStd]
2021-03-10 fix bug on board, upload some documents, clean up repo (delete unused folders) and upload some iterations of the printed body
    [1-click-bom.tsv, 1-click-bom_old.csv, DIGIKEY_BOM_TEMP.csv, LHDA3D00006AA - PRTD - 3Way,2Way - V1.step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]
2021-04-19 fix orientation of valves and diameter of opening
    [electronics_box.FCStd, main.FCStd, main_body.scad, main_body.stl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]
2021-04-20 main block updates: side channels inside block now leave at an angle to facilitate 3D printing and valves are positioned at 45 degrees. This enables valves to be placed 'upside down' so that exhaust 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
    [main_body.scad, main_body.stl, main_body_cutout1.stl, main_body_half.stl]
2021-04-27 make fittings for rotameters and tubes
    [flow_to_tube_connectors.scad, flow_to_tube_connectors.stl]
2021-04-27 resolve flowmeter to tube adapter
    [flow_to_tube_connectors.scad, flow_to_tube_connectors.stl]
2021-04-28 final cleanup on printed parts for attaching tubes to flowmeters
    [flow_to_tube_connectors.stl, flowmeter_holder.scad, y_connectors.scad, y_connectors.stl]
2021-04-28 rearrange folder structure
    [flow_to_tube_connectors.stl, main.FCStd, main_body.stl, main_body_cutout1.stl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]
2021-05-05 remove excessive track on board (two ground tracks going to same place), add + sign on polar capacitors, add 3D models for connectors
    [flow_to_tube_connectors.scad, flow_to_tube_connectors_large.stl, spike_n_hold-B_Adhes.gbr, spike_n_hold-B_CrtYd.gbr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]
2021-05-18 updated mechanics
    [main_body.scad, main_body.stl, y_connectors.scad]
2021-05-18 upload stl
    [main_body_w_holder.stl]
2021-08-20 updated version of central block
    [carburator.scad, dilution_block.scad, main_body.scad, main_body.stl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]
2021-11-03 adapt main body for thinner input tubes
    [main_body.3mf, main_body.scad]
2021-12-07 update main block
    [main_body.3mf, main_body.scad, main_body.stl]

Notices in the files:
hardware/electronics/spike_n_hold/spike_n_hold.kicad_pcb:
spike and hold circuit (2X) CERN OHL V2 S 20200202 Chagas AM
